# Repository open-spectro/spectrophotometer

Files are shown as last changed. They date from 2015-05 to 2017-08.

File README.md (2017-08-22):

# Learning spectrophotometry

## Introduction

You can find very expensive and powerful 
spectrophotometer on the market but for teaching they are most
of the time a black box that can not be open.

In order to be able to better teach the technique we would
like to create a simple, open source, spectrophotometer.

The idea is relatively simple. You have 4 leds (red, green,
blue, white) that can be turned on / off. The beam will
cross a cell, go through a slit and is diffracted using a
grating film.

A linear sensor allows to analyze the intensity of each
resulting wavelength.

There are 4 main parts in this project
* the electronic and microcontroller
* the microcontroller firmware
* the box
* the end-user graphical interface

Thanks to a google chrome "apps" it is possible directly from the web-browser to control the instrument. The application is available for [free on the store](https://chrome.google.com/webstore/detail/open-spectrophotometer/bmkhbnoonjkmdlkfncokjkanfgilppkn).

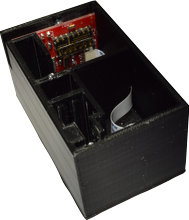
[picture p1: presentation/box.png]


## Electronic and microcontroller

We played for a while with the Arduino platform and quickly
found out that you can relatively easily create your own
board that is compatible with the Arduino software.

This means that all the electronic can be designed to fit
exactly your needs but you will still be able to program
the device using the [Arduino](http://www.arduino.cc/).

The linear sensor is based on the linear sensor array 
[TSL1402R](http://ams.com/content/download/250165/975693/TSL1402R_Datasheet_EN_v1.pdf).

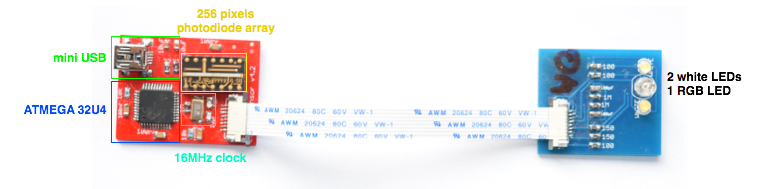
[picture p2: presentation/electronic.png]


### Buttons

In order to prevent any problems with mechanical buttons and
buttons on the service, capasitive sensors are considered.

http://playground.arduino.cc/Main/CapacitiveSensor?from=Main.CapSense

## Firmware

The device emulates an Arduino Leonardo and can therefore be
programmed using the USB cable using the
[Arduino software](http://www.arduino.cc/en/Main/Software). We 
currently use version 1.0.6.

The first tie the bootloader has to be installed on the
microcontroller ATMega32U4.

## The box

To create the box we are using:
* [123D design](http://www.123dapp.com/design)
* [Robox 3D printer](http://www.cel-robox.com/)

## End-user graphical interface

The user interface is based on the 
[Visualizer](http://github.com/npellet/visualizer) and is available on the [Google Apps store](https://chrome.google.com/webstore/detail/open-spectrophotometer/bmkhbnoonjkmdlkfncokjkanfgilppkn)

## Control from the terminal (Advanced users)

From a terminal on the macintosh you could currently do something like

``` screen /dev/tty.usbmodemfdXXX 115200 ```

(you need to find the correct tty device using 

``` ls /dev/tty.usb* ```

To kill this session

``` CTRL + a and then k ```

You are then in the terminal menu and you can enter

```h + enter```

For the various options.

To take a spectrum:

```r + enter```

You will then have 10s (blue blinking) to put the reference sample.
Once the green flash appears you have 10s to put the sample.

All the results may be pasted in a view:

http://www.cheminfo.org/Spectra/Spectrophotometer/Test.html

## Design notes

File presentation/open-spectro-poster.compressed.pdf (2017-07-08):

## Open hardware, open software https://github.com/open-spectro

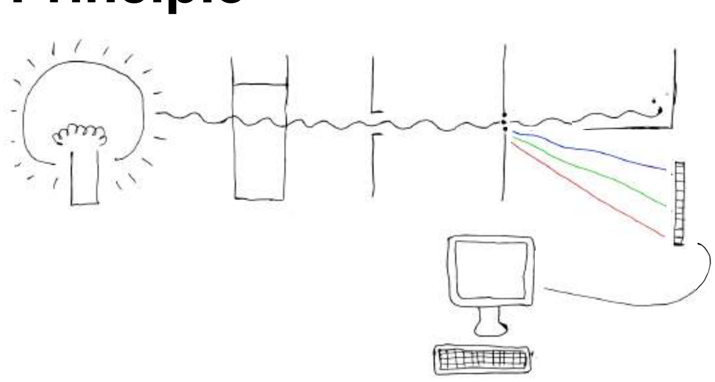
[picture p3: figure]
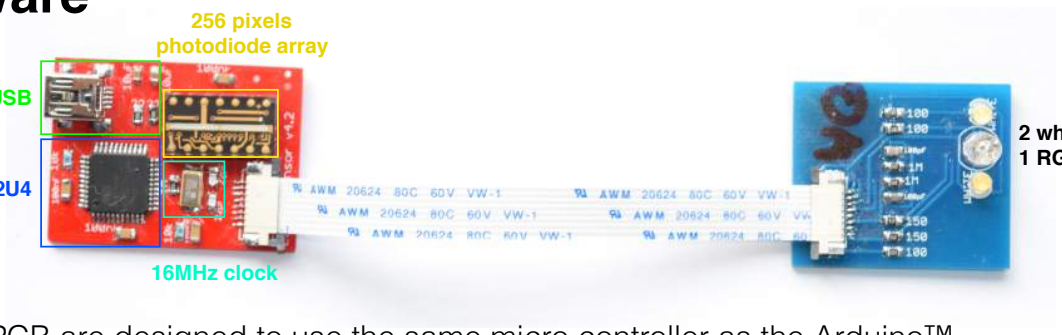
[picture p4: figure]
16MHz clock; 256 pixels photodiode array

mini USB

ATMEGA 32U4

### 2 white LEDs 1 RGB LED

# HOW ?

# open-spectrophotometer

Florian, Océane and Luc Patiny, Michaël Zasso

The light produced by white LEDs goes through a sample, is selected by 2 slits and diffracted by a grating film. The diffracted light is analysed by a photodiode array that is connected to the computer.

Compact PCB are designed to use the same micro controller as the Arduino™ Leonardo and is fully compatible with the Arduino™ IDE. This makes it very easy to program.
Communication with the spectrophotometer is done using USB virtual serial port allowing simple control from any program.

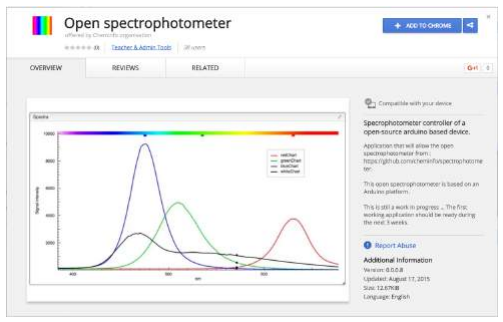
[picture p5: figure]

A chrome application allows to control directly the spectrophotometer from the computer in order to calibrate, acquire and process the data.

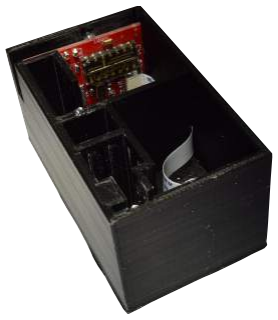
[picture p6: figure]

3D printed box with a
precision of 0.1 mm
allows precise installation of the electronic and
grating film.

## Principle

## Hardware

## Software

# open-spectrophotometer

# WHAT FOR ?

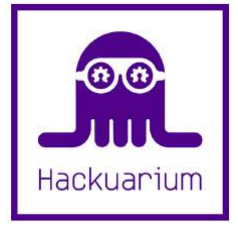
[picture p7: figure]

## Simple design to understand how a spectrophotometer

works, but precise enough to make real experiments. Very cheap and accessible to everyone.

## Determination of pigments concentration

## Determination of pH using red cabbage

Chopped red cabbage was cooked in boiling water for 10 minutes to yield after filtration to a dark purple liquid.
The liquid was diluted by a factor 3 with water and either tartaric acid or sodium carbonate where added in various quantities to obtain a large color palette.
Red: acid, green: basic | Absorbance spectra of the 9 solutions

Linear regression

Slope: 46.12
Intercept: 0.03
R: 0.9973
R²: 0.9946

Blue patent V is the pigment that is present in Haribo smurfs sweets. Using a calibration curve with the pure pigment it is possible to determine the amount of colorant present in the sweets.

Left: reference solutions. Right: Haribo | Calibration curve. In red the unknown.

Florian, Océane and Luc Patiny, Michaël Zasso

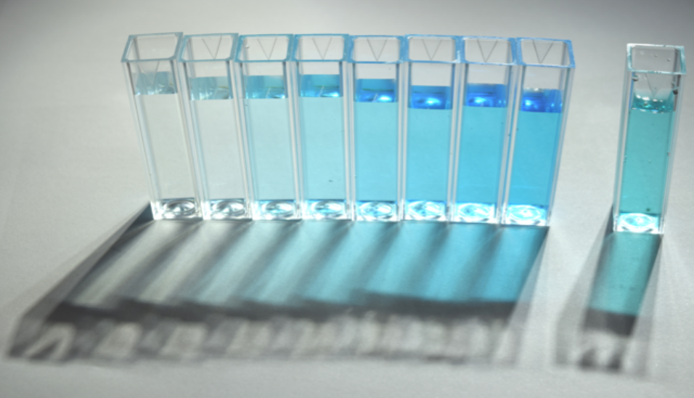
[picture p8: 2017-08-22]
presentation/blue.png

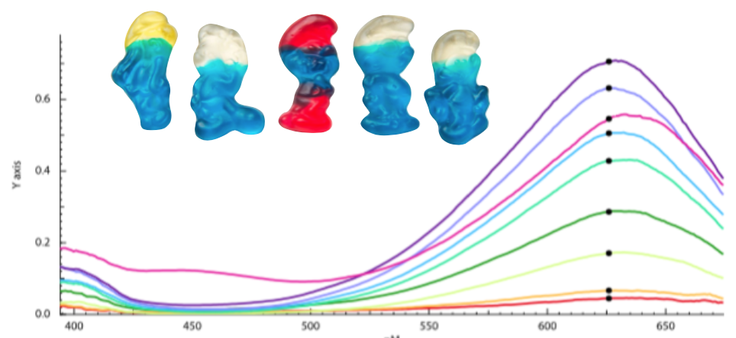
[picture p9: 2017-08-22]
presentation/smurf.png

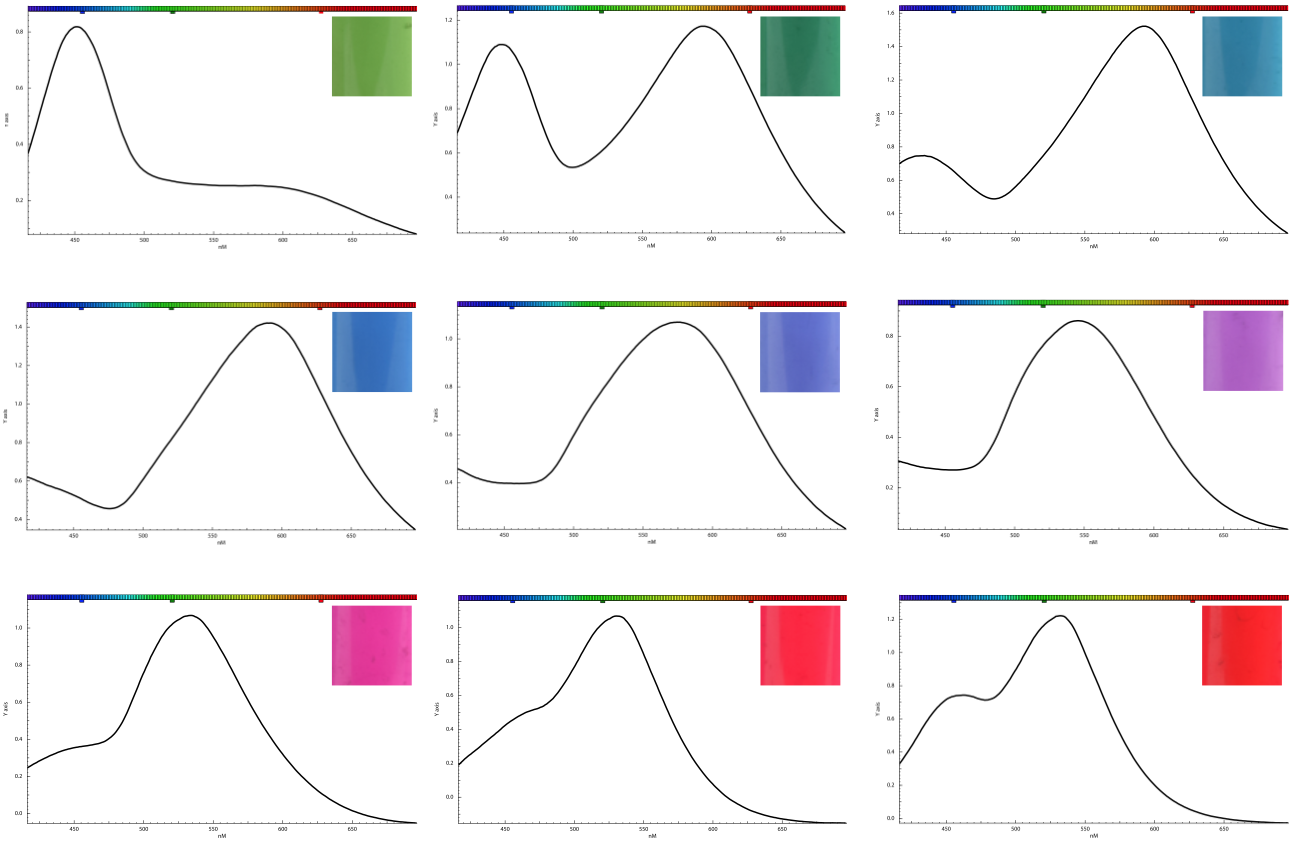
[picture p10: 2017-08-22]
presentation/cabbage.png

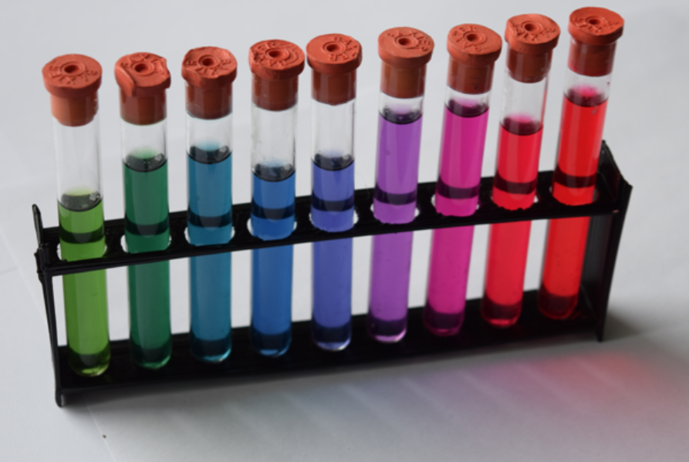
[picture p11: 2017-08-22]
presentation/cabbage2.png

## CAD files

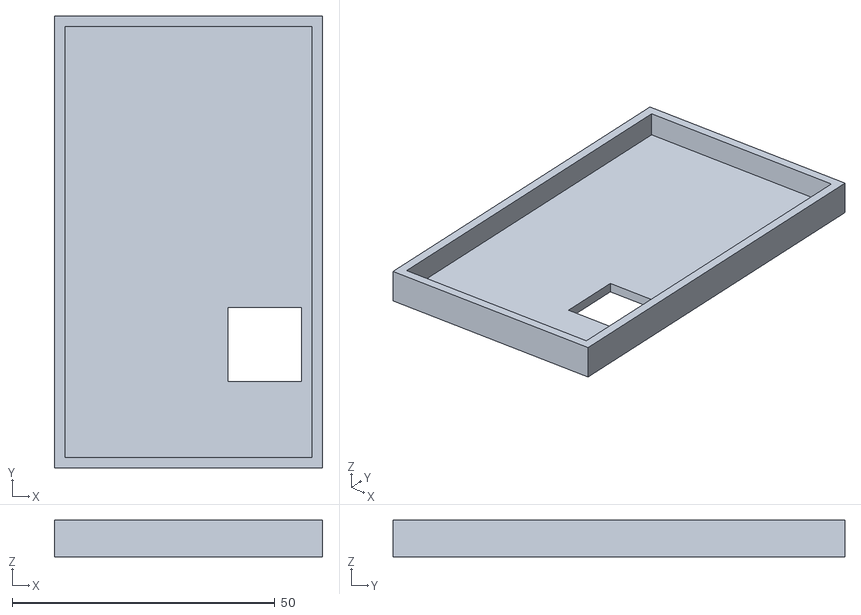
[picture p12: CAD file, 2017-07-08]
cad/top.stl
51.0 x 86.0 x 7.00

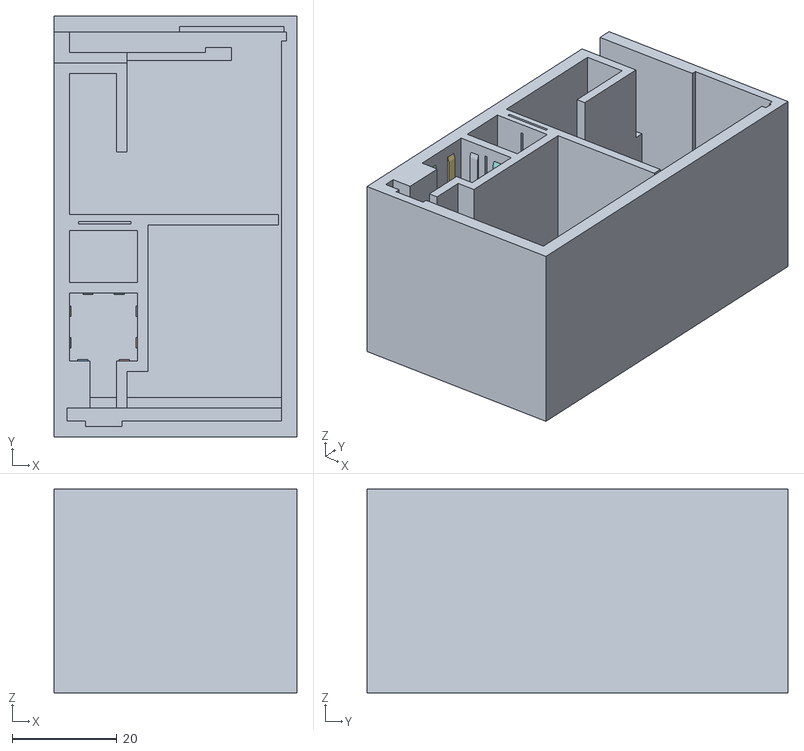
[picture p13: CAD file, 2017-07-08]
cad/model.stl
46.5 x 80.5 x 39.0

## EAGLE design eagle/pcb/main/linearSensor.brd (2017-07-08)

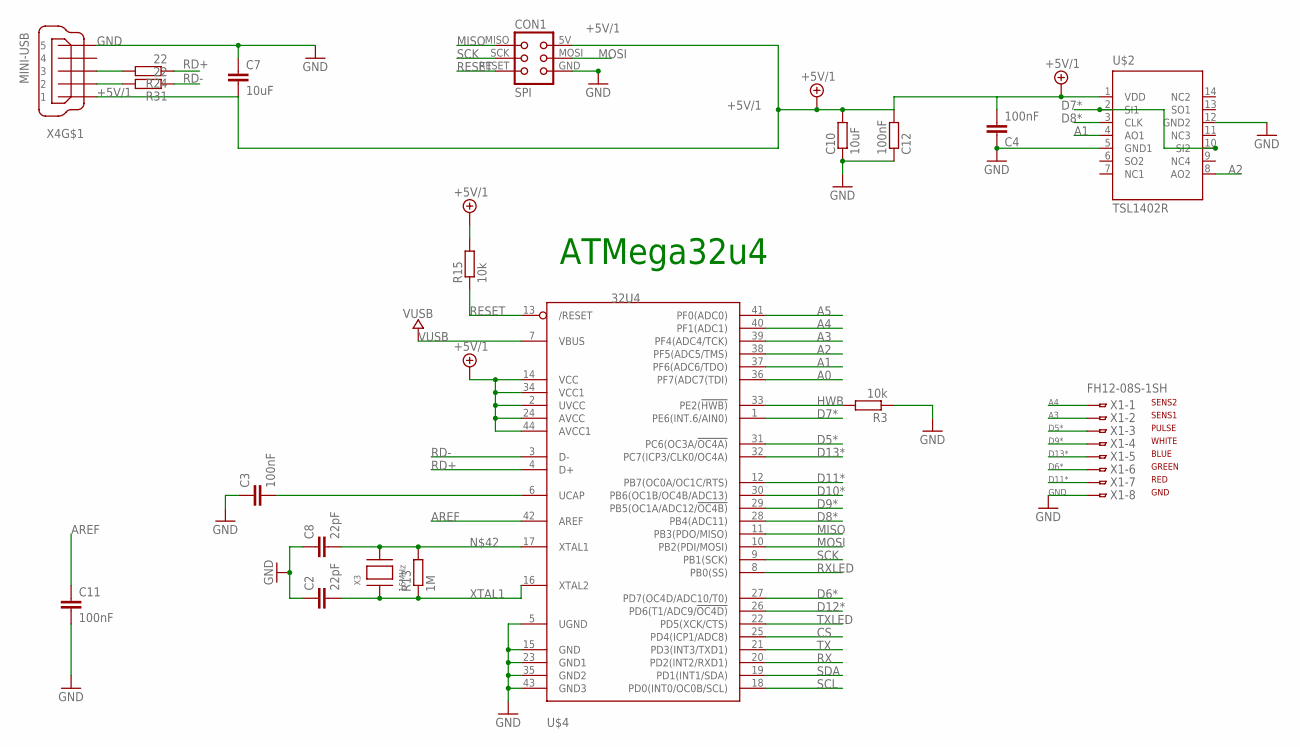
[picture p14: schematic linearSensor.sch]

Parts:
C2, C8: 22pF; C0805K
C3, C11: 100nF; C0805K
C4: 100nF; C0805
C7: 10uF; C0805
C10: 10uF; M0805
C12: 100nF; M0805
CON1: SPI; TC2030-MCP-NL
R3, R15: 10k; M0805
R13: 1M; M0805
R24, R31: 22; M0805
U$2: TSL1402R; DIL14
U$4: 32U4; TQFP44
X1: FH12-08S-1SH
X3: 16MHz; NX6035
X4: MINI-USB; 32005-201

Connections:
+5V/1: C4.2, C7.2, C10.2, C12.2, CON1.5V (VCC), R15.2, U$2.1 (VDD), U$4.2 (UVCC), U$4.14 (VCC), U$4.24 (AVCC), U$4.34 (VCC1), U$4.44 (AVCC1), X4.1
A0: U$4.36 (PF7(ADC7(TDI))
A1: U$2.4 (AO1), U$4.37 (PF6(ADC6/TDO))
A2: U$2.8 (AO2), U$4.38 (PF5(ADC5/TMS))
A3: U$4.39 (PF4(ADC4/TCK)), X1.2
A4: U$4.40 (PF1(ADC1)), X1.1
A5: U$4.41 (PF0(ADC0))
AREF: C11.1, U$4.42 (AREF)
CS: U$4.25 (PD4(ICP1/ADC8))
D5*: U$4.31 (PC6(OC3A/!OC4A)), X1.3
D6*: U$4.27 (PD7(OC4D/ADC10/T0)), X1.6
D7*: U$2.2 (SI1), U$2.10 (SI2), U$4.1 (PE6(INT.6/AIN0))
D8*: U$2.3 (CLK), U$4.28 (PB4(ADC11))
D9*: U$4.29 (PB5(OC1A/ADC12/!OC4B)), X1.4
D10*: U$4.30 (PB6(OC1B/OC4B/ADC13))
D11*: U$4.12 (PB7(OC0A/OC1C/RTS)), X1.7
D12*: U$4.26 (PD6(T1/ADC9/!OC4D))
D13*: U$4.32 (PC7(ICP3/CLK0/OC4A)), X1.5
D_USB+: R24.2, X4.3
D_USB-: R31.2, X4.2
GND: C2.1, C3.1, C4.1, C7.1, C8.1, C10.1, C11.2, C12.1, CON1.GND, R3.1, U$2.5 (GND1), U$2.12 (GND2), U$4.5 (UGND), U$4.15 (GND), U$4.23 (GND1), U$4.35 (GND2), U$4.43 (GND3), X1.8, X4.5
HWB: R3.2, U$4.33 (PE2(!HWB))
MISO: CON1.MISO, U$4.11 (PB3(PDO/MISO))
MOSI: CON1.MOSI, U$4.10 (PB2(PDI/MOSI))
unnamed: C3.2, U$4.6 (UCAP)
unnamed: C8.2, R13.2, U$4.17 (XTAL1), X3.P$2
RD+: R24.1, U$4.4 (D+)
RD-: R31.1, U$4.3 (D-)
RESET: CON1.RESET, R15.1, U$4.13 (/RESET)
RX: U$4.20 (PD2(INT2/RXD1))
RXLED: U$4.8 (PB0(SS))
SCK: CON1.SCK, U$4.9 (PB1(SCK))
SCL: U$4.18 (PD0(INT0/OC0B/SCL))
SDA: U$4.19 (PD1(INT1/SDA))
TX: U$4.21 (PD3(INT3/TXD1))
TXLED: U$4.22 (PD5(XCK/CTS))
VUSB: U$4.7 (VBUS)
XTAL1: C2.2, R13.1, U$4.16 (XTAL2), X3.P$1

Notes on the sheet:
ATMega32u4
GND
RED
GREEN
BLUE
WHITE
PULSE
SENS1
SENS2

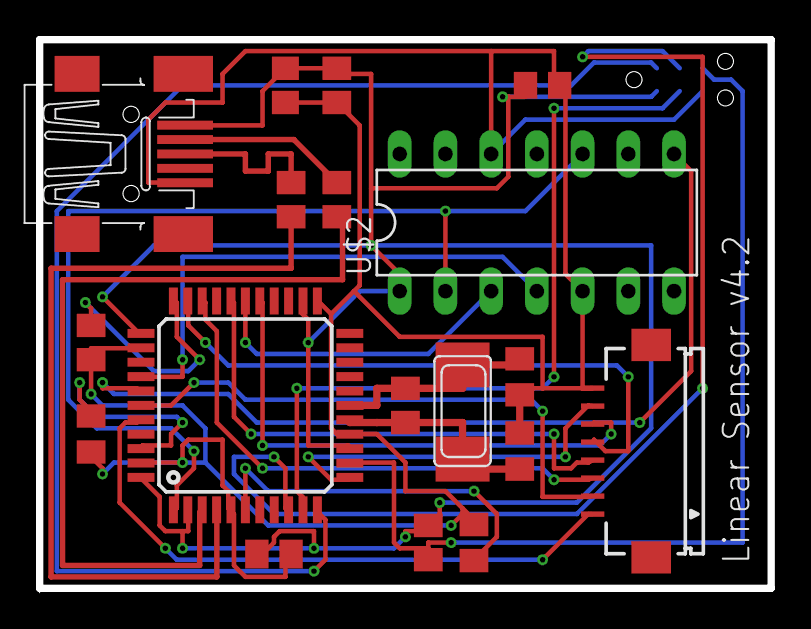
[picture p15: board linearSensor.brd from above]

Board: 2 copper layers, 40.6 x 30.5 mm, 19 parts (1 on the bottom side), 26 nets.

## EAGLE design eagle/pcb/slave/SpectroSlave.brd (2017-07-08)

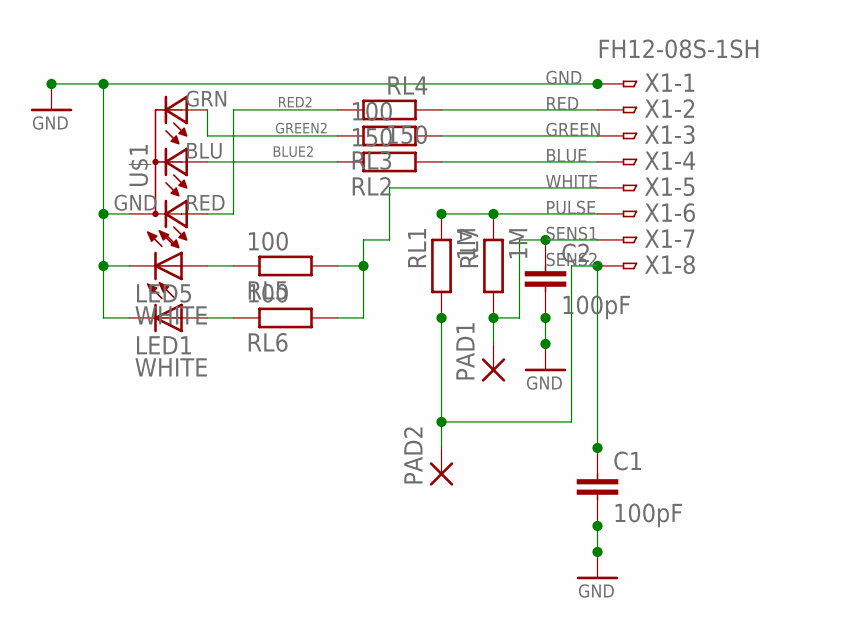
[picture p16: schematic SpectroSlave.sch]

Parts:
C1, C2: 100pF; C0805
LED1, LED5: WHITE; LED3MM
PAD1, PAD2: SMD5; SMD2,54-5,08
RL1, RL7: 1M; R0805
RL2, RL4: 150; R0805
RL3, RL5, RL6: 100; R0805
U$1: RGB-COMMON-CATHODE; LED-TRICOLOR-THROUGHHOLE
X1: FH12-08S-1SH

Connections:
BLUE: RL2.2, X1.4
BLUE2: RL2.1, U$1.BLU (CBLUE)
GND: C1.2, C2.2, LED1.K (C), LED5.K (C), U$1.GND (A2), X1.1
GREEN: RL3.2, X1.3
GREEN2: RL3.1, U$1.GRN (CGREEN)
unnamed: LED5.A, RL5.1
unnamed: LED1.A, RL6.1
PULSE: RL1.1, RL7.1, X1.6
RED: RL4.1, X1.2
RED2: RL4.2, U$1.RED (CRED)
SENS1: C2.1, PAD1.1, RL7.2, X1.7
SENS2: C1.1, PAD2.1, RL1.2, X1.8
WHITE: RL5.2, RL6.2, X1.5

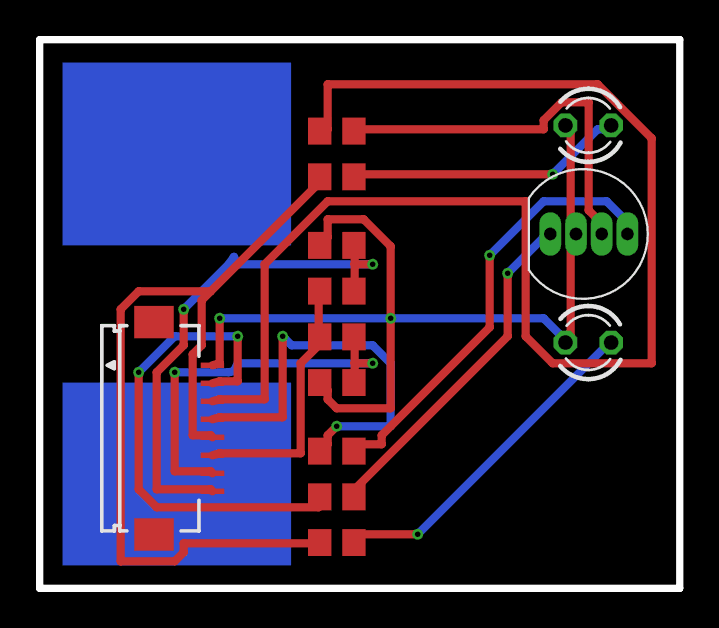
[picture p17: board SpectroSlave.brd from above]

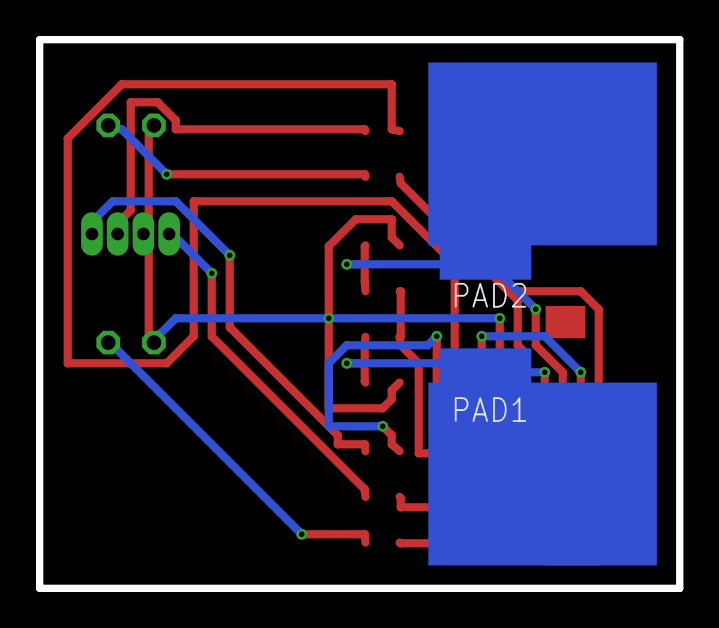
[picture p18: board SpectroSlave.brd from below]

Board: 2 copper layers, 35.6 x 30.5 mm, 15 parts (2 on the bottom side), 13 nets.

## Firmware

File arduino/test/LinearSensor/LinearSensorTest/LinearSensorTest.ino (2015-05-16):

#define ARRAY_SIZE 256
#define AVERAGE 0

#define AO_PIN1 A1
#define AO_PIN2 A2
#define INTEGRATION_TIME 20

#define REPEAT_ACQUISITION 63  // max value=63 !!!!
#define REPEAT_CALIBRATE  10  // max value=63 !!!!
#define SMOOTH_CALIBRATE  15  // max value=63 !!!!
#define RED    11
#define GREEN   6
#define BLUE   13
#define UV     10
#define WHITE   9

#define CLKpin  8    // <-- Arduino pin delivering the clock pulses to pin 3 (CLK) of the TSL1402R 
#define SIpin   7     // <-- Arduino pin delivering the SI (serial-input) pulse to pin 2 of the TSL1402R 


byte RGB[]={
  RED, GREEN, BLUE};
byte LEDS[]={
  RED, GREEN, BLUE, WHITE, UV      };
char INFO[]={
  'R','G','B','W','U','Z','E' }; // E: experiment, Z: reference

byte pointRed=0;
byte pointGreen=0;
byte pointBlue=0;

void setup() 
{
  delay(5000);
  Keyboard.begin();
  Serial.begin(115200);

initLinear();

  // Next, assert default setting:
  analogReference(DEFAULT);

  pinMode(RED, OUTPUT);
  pinMode(GREEN, OUTPUT);
  pinMode(BLUE, OUTPUT);
  pinMode(WHITE, OUTPUT);
  pinMode(UV, OUTPUT);
}

void loop() 
{  
  calibrate();

  // realExperiment();

  //testAllColors();
   testGreenIntensity();
  // fullOn();

}


void fullOn() {
  for (byte i=0; i<sizeof(LEDS); i++) {
    digitalWrite(LEDS[i], HIGH);
  }
}

void testAllColors() {
  for (byte i=0; i<sizeof(LEDS); i++) {
    unsigned int signalArray[ARRAY_SIZE]; // <-- the array where the readout of the photodiodes is stored, as integers
    unsigned int backgroundArray[ARRAY_SIZE];
    byte channel=LEDS[i];
    int currentIntensity=autoIntensity(channel);
    acquire(signalArray, channel);
    analogWrite(channel, 0);
    acquire(backgroundArray, channel);
    diffArray(signalArray, backgroundArray);
    printResult(&Serial, signalArray, backgroundArray, i, currentIntensity, AVERAGE);
  }
}

void realExperiment() {
  // we will use the white led
  // we make a spectrum
  unsigned int signalArray[ARRAY_SIZE]; // <-- the array where the readout of the photodiodes is stored, as integers
  unsigned int backgroundArray[ARRAY_SIZE];

  for (int i=0; i<10; i++) {
    analogWrite(BLUE, 255);
    delay(500);
    analogWrite(BLUE, 0);
    delay(500);
  }

  int currentIntensity=autoIntensity(WHITE);
  acquire(signalArray, WHITE);
  analogWrite(WHITE, 0);
  acquire(backgroundArray, WHITE);
  diffArray(signalArray, backgroundArray);
  printResult(&Serial, signalArray, backgroundArray, 5, currentIntensity, AVERAGE);

  for (int i=0; i<10; i++) {
    analogWrite(GREEN, 255);
    delay(500);
    analogWrite(GREEN, 0);
    delay(500);
  }

  analogWrite(WHITE, currentIntensity-1);
  acquire(signalArray, WHITE);
  analogWrite(WHITE, 0);
  acquire(backgroundArray, WHITE);
  diffArray(signalArray, backgroundArray);
  printResult(&Serial, signalArray, backgroundArray, 6, currentIntensity, AVERAGE);

}


void testGreenIntensity() {
  int intensity=256;
  for (byte i=0; i<6; i++) {
    unsigned int signalArray[ARRAY_SIZE]; // <-- the array where the readout of the photodiodes is stored, as integers
    unsigned int backgroundArray[ARRAY_SIZE];
    byte channel=GREEN;
    analogWrite(channel, intensity-1);
    acquire(signalArray, channel);
    analogWrite(channel, 0);
    acquire(backgroundArray, channel);
    diffArray(signalArray, backgroundArray);
    printResult(&Serial, signalArray, backgroundArray, 1, intensity, AVERAGE);
    intensity/=2;
  }
}

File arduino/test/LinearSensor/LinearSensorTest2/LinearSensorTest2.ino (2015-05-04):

// Parallel read of the linear sensor array TSL1402R (= the sensor with 256 photodiodes)
//-------------------------------------------------------------------------------------

// Define various ADC prescaler:
const unsigned char PS_32 = (1 << ADPS2) | (1 << ADPS0);
const unsigned char PS_128 = (1 << ADPS2) | (1 << ADPS1) | (1 << ADPS0);

int CLKpin = 8;    // <-- Arduino pin delivering the clock pulses to pin 3 (CLK) of the TSL1402R 
int SIpin = 7;     // <-- Arduino pin delivering the SI (serial-input) pulse to pin 2 of the TSL1402R 
int AOpin1 = A1;    // <-- Arduino pin connected to pin 4 (analog output 1)of the TSL1402R
int AOpin2 = A2;    // <-- Arduino pin connected to pin 8 (analog output 2)of the TSL1402R
int IntArray[256]; // <-- the array where the readout of the photodiodes is stored, as integers
int counter=0;

#define RED    11
#define GREEN   6
#define BLUE   13
#define UV     10
#define WHITE   9


void setup() 
{
  delay(100);
  
  // Initialize two Arduino pins as digital output:
  pinMode(CLKpin, OUTPUT); 
  pinMode(SIpin, OUTPUT);  

  // To set up the ADC, first remove bits set by Arduino library, then choose 
  // a prescaler: PS_16, PS_32, PS_64 or PS_128:
  /*
  ADCSRA &= ~PS_128;  
  ADCSRA |= PS_32; // <-- Using PS_32 makes a single ADC conversion take ~30 us
*/
  // Next, assert default setting:
  analogReference(DEFAULT);


  Serial.begin(115200);
}

void loop() 
{  
  counter++;
  // Stop the ongoing integration of light quanta from each photodiode by clocking in a SI pulse 
  // into the sensors register:
  resetClockPulse();

  // Next, read all 256 pixels in parallell. Store the result in the array. Each clock pulse 
  // causes a new pixel to expose its value on the two outputs:
  long start=micros();
  for(int i=0; i < 128; i++)
  {
    delayMicroseconds(20);// <-- We add a delay to stabilize the AO output from the sensor
    IntArray[i] = analogRead(AOpin1);
    IntArray[i+128] = analogRead(AOpin2);
    clockPulse(); 
  }

// should we increase the integration time ????
  for(int i=0; i < 128; i++)
  {
        clockPulse(); 
  }


  if (counter==200) {
    counter=0;
    Serial.print("Reading time: ");
    Serial.println(micros()-start);
    printResult(false);
  }

}

// This function generates an outgoing clock pulse from the Arduino digital pin 'CLKpin'. This clock
// pulse is fed into pin 3 of the linear sensor:
void clockPulse()
{
  delayMicroseconds(1);
  digitalWrite(CLKpin, HIGH);
  delayMicroseconds(1);
  digitalWrite(CLKpin, LOW);
}

void resetClockPulse()
{
  delayMicroseconds(1);
  digitalWrite(SIpin, HIGH);
  delayMicroseconds(1);
  digitalWrite(CLKpin, HIGH);
  delayMicroseconds(1);
  digitalWrite(SIpin, LOW);
  delayMicroseconds(1);
  digitalWrite(CLKpin, LOW);
}


void printResult(boolean printId) {
  Serial.println("V2");
  // Next, send the measurement stored in the array to host computer using serial (rs-232).
  // communication. This takes ~80 ms during whick time no clock pulses reaches the sensor. 
  // No integration is taking place during this time from the photodiodes as the integration 
  // begins first after the 18th clock pulse after a SI pulse is inserted:
  for(int i = 0; i < 256; i++)
  {
    if (printId) {
      if (i<10) Serial.print(" ");
      if (i<100) Serial.print(" ");
      Serial.print(i);
      Serial.print(" : ");
    }
    if (IntArray[i]<10) Serial.print(" ");
    if (IntArray[i]<100) Serial.print(" ");
    if (IntArray[i]<1000) Serial.print(" ");
    Serial.print(IntArray[i]);

    if (i%16 == 15) {
      Serial.println("");
    }
    else {
      Serial.print(" - ");
    }
  }
  Serial.println(""); // <-- Send a linebreak to indicate the measurement is transmitted.
}

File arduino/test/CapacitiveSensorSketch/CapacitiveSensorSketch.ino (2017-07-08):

#include <CapacitiveSensor.h>

/*
 * CapitiveSense Library Demo Sketch
 * Paul Badger 2008
 * Uses a high value resistor e.g. 10M between send pin and receive pin
 * Resistor effects sensitivity, experiment with values, 50K - 50M. Larger resistor values yield larger sensor values.
 * Receive pin is the sensor pin - try different amounts of foil/metal on this pin
 */

CapacitiveSensor   sensor1 = CapacitiveSensor(5,A3);        // 10M resistor between pins 4 & 2, pin 2 is sensor pin, add a wire and or foil if desired

CapacitiveSensor   sensor2 = CapacitiveSensor(5,A4);        // 10M resistor between pins 4 & 2, pin 2 is sensor pin, add a wire and or foil if desired


void setup()                    
{
  Serial.begin(115200);
  pinMode(13, OUTPUT);     
   pinMode(6, OUTPUT);   
}

long previous1=0;
long difference1=0;
long previous2=0;
long difference2=0;

void loop()                    
{
  long start = millis();

  long total1 =  sensor1.capacitiveSensor(50);
  difference1=total1-previous1;
  previous1=total1;

  long total2 =  sensor2.capacitiveSensor(50);
  difference2=total2-previous2;
  previous2=total2;

  Serial.print(millis() - start);        // check on performance in milliseconds
  Serial.print("\t");                    // tab character for debug windown spacing
  Serial.print(total1);                  // print sensor output 1
  Serial.print("\t");                    // tab character for debug windown spacing
  Serial.print(difference1);                  // print sensor output 1
  Serial.print("\t");                    // tab character for debug windown spacing
  Serial.print(total2);                  // print sensor output 1
  Serial.print("\t");                    // tab character for debug windown spacing
  Serial.println(difference2);                  // print sensor output 1
  if (total1>200) {
    digitalWrite(13, HIGH);
  } 
  else {
    digitalWrite(13, LOW);
  }
  if (total2>200) {
    digitalWrite(6, HIGH);
  } 
  else {
    digitalWrite(6, LOW);
  }
  delay(50);                             // arbitrary delay to limit data to serial port 
}

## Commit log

2014-11-15 First release
    [linearSensor.brd, linearSensor.sch, v1.GBL, v1.GBO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]
2014-11-15 Add first files
    [Box drawing.brd, SpectroSlave.brd, SpectroSlave.sch, linearSensor.brd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]
2015-05-04 Refactor the code to allow more possibilities Show linearity of the detector
    [Box drawing.brd, SpectroSlave.brd, linearSensor.brd]
2015-05-08 Add 3D model
    [SpectroSlave.brd, SpectroSlave.sch, model1.stl, model2.stl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]
2015-05-08 Add the cover
    [box.stl]
2015-05-16 Improve box
    [linearSensor.brd, model5.stl, top-5.stl]
2015-05-23 Add new salve and capacitive sensor sketch
    [SpectroSlave.brd, SpectroSlave.sch]
2015-08-12 Add working example of the arduino board control
2015-08-14 Add possibility to turn on / off leds
2015-08-15 New spectrophotometer board
    [SpectroSlave.brd, linearSensor.brd, linearSensor.sch]
2015-08-18 split the project
    [Box drawing.brd, SpectroSlave.brd, SpectroSlave.sch, box.stl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]
2017-07-08 Moved for eagle and arduino projects
    [SpectroSlave.brd, SpectroSlave.sch, linearSensor.brd, linearSensor.sch]
2017-07-08 Add box
    [model.stl, top.stl]

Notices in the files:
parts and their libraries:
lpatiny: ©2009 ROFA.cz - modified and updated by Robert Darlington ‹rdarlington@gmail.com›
